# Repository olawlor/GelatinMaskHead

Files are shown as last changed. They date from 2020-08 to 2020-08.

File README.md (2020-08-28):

# Gelatin Mask-testing Head
For quantitative testing of masks, the standard NIOSH head models are made from solid rigid plastic.  Because this does not at all resemble human skin, the NIOSH N95 testing protocol allows the use of rope caulk and tape to provide a tight seal, which is not a good approximation for a human face.

This project contains a 3D printed set of parts and molds for casting a gelatin face for testing masks.  Because the face is cast from soft flexible gelatin, this better matches the compliance of a human face, which should give more accurate results when testing masks for fit and filtering effectiveness.

The face outer surface is currently built around the NIOSH "medium" head profile.

See the NioshMedium/ directory for CAD files of:
 * The "Head" without a face.  The head is normally printed from rigid plastic and holds the face in place, and provides a place for mask straps to attach.  There is a six-bolt hole pattern in the bottom of the head for mounting it into a test apparatus.  The top of the head is open to allow access to the back of the face, such as flowing in aerosols.
 * The "Skull" that gets bolted inside the face area.  This is printed from rigid plastic, and models the actual human skull areas that support the face while wearing a mask.
 * The "Overmold" is used to cast gelatin onto the skull while mounted on the head.
 
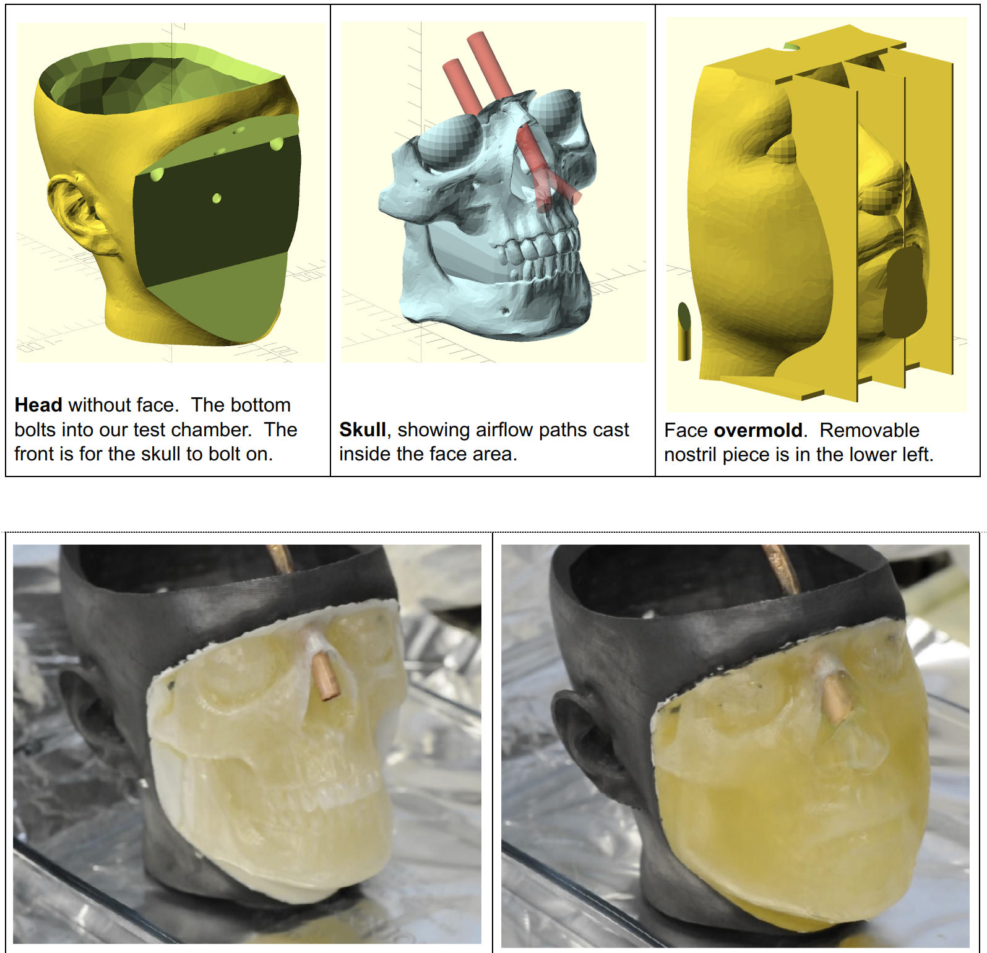
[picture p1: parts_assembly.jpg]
Components to 3D print, and the resulting molded head.


All of these parts should be printed as smooth and watertight as possible--casting gelatin will leak into non-watertight areas, resulting in much larger gelatin consumption.  The no-leak gelatin volume is 310cc, but 500cc is reasonable to account for leaks and spills.  Pre-chilling the mold can help somewhat with leaks.

After printing, the face overmold should be sealed and smoothed by applying several layers of high-build automotive primer paint.  A release layer of vaseline dissolved in volatile lamp oil should be applied to the inside of the face overmold.  The skull is then bolted to the face with a ¼" or 6mm plastic bolt (plastic is preferred over metal to reduce galvanic effects around the salty gelatin).

The air inlet tubes for the nostril or mouth inlets are ⅜" or 10mm outside diameter.  Conductive silicone is recommended: nonconductive plastic can accumulate an electrostatic charge, and metals can corrode.  The air inlet tub is inserted and aligned with the nostril plugs (verify inlet to nostril alignment with a lamp behind the overmold before pouring).  The inlet tube should be filled with a temporary ¼" or 6mm plastic tube to prevent it from getting filled with gel during casting.

The castable gelatin face composition is primarily water, with:
 * 10% w/v gelatin (Knox gelatin.  10% is the US federal standard ballistics testing gelatin concentration but is rather delicate; it may be worthwhile to upgrade this to 20% NATO gelatin for better handling properties.)
 * 10% w/v table salt, for electrical conductivity and biological decay resistance
 * 1% w/v sodium bicarbonate, to remain alkaline which increases the gelatin strength and reduces metal corrosion from the salt.  The solution is still quite corrosive, even to copper.

Casting protocol:
 * Mix gelatin with cold (5C) water first (like flour, the outside of a dry area will gel and prevent water accessing the interior unless you start cold).
 * Heat the gelatin to 45C, stir until gelatin is fully dissolved, add salt, stir until fully dissolved, filter
 * Ensure the overmold is face-down, with the head and skull inserted completely, and the nostril inlet tube aligned with the nostril plugs.
 * Carefully pour gelatin into the mold at about 30C gelatin temperature.
 * Chill the mold 10C for several hours to fully solidify before demolding.  The head needs to be treated gently, and kept in a cool environment: in a warm sunbeam for several hours it will melt off the skull.

Spray a clear rubbery sealant (Rustoleum LeakSeal, clear) directly onto the gelatin surface of the face to create a thin (approx 0.2mm) "skin" layer over the gelatin.  This substantially reduces abrasion damage to the face's surface while putting masks on and taking masks off, and has the added benefit of reducing water evaporation losses from the gelatin surface.  Masks also seem to seal better (by about 10%) against this surface than the bare gelatin.

The salt makes the face electrically conductive, but the plastic of the head is nonconductive, and hence static susceptible.  To reduce static, the hard plastic parts were fully painted in a dark graphite slurry consisting of:
 * Conductive finely ground graphite (agricultural EZ-Slide brand)
 * Acetone solvent
 * ABS 3D printer filament, chopped into pieces and dissolved into the acetone, to bind the dried graphite.
This combines to a sort of thin paint, although the graphite settles out rapidly and must be stirred up regularly.  Apply this fairly heavily and then buff off excess with steel wool, making a dark and rather metallic looking finish that electrically reads in the kilo-ohm range.

Explanation of these files and initial mask testing results are here:
https://docs.google.com/document/d/1Q9jaSaZRyKj-hi1BDpFaLHJNcuCx2OrSKFoyBqVJWUo/edit

"Human_Skull_Scan_fixed2" is a human skull model, license CC-A-NC, modified from:
    https://www.thingiverse.com/thing:2368585

This model was prepared by Orion Lawlor, lawlor@alaska.edu, in summer 2020 to help with COVID prevention.  Support for this project has been provided by the Office of Naval Research.

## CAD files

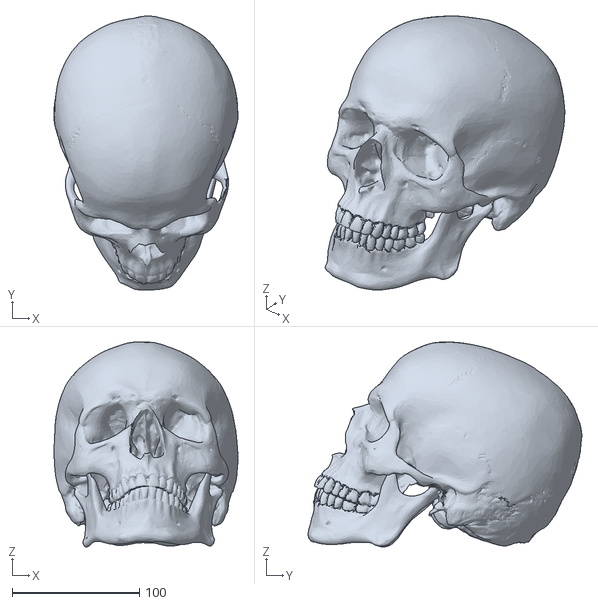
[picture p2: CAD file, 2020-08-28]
Human_Skull_Scan_fixed2.stl
144.8 x 215.6 x 161.4

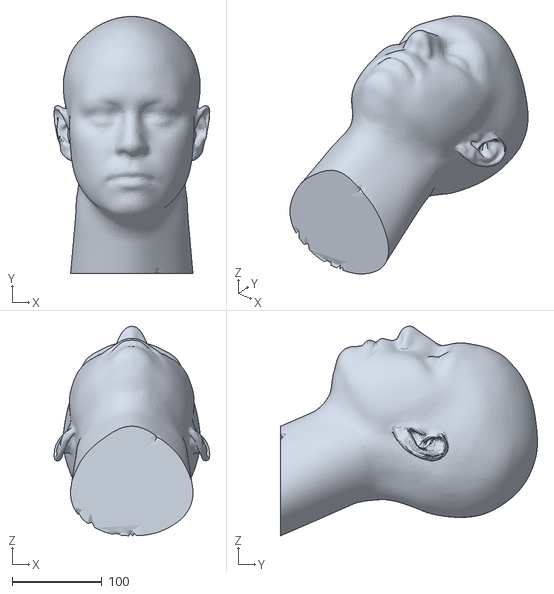
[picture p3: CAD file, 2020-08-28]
NioshMedium/8-NIOSH_medium_20k.stl
173.0 x 285.7 x 233.0

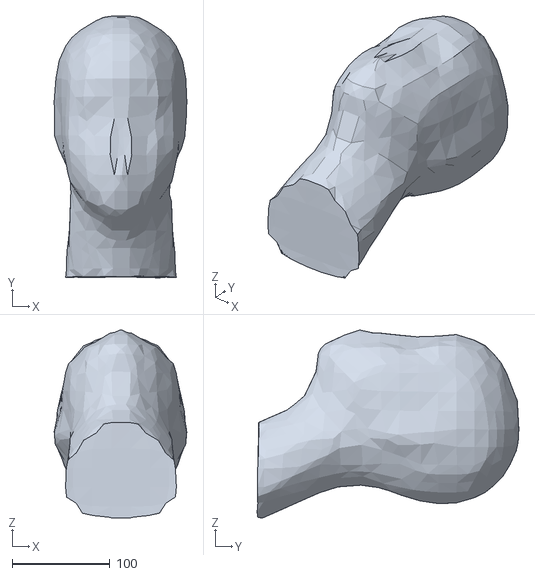
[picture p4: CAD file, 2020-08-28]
NioshMedium/8-NIOSH_medium_interior.stl
135.8 x 268.0 x 192.5

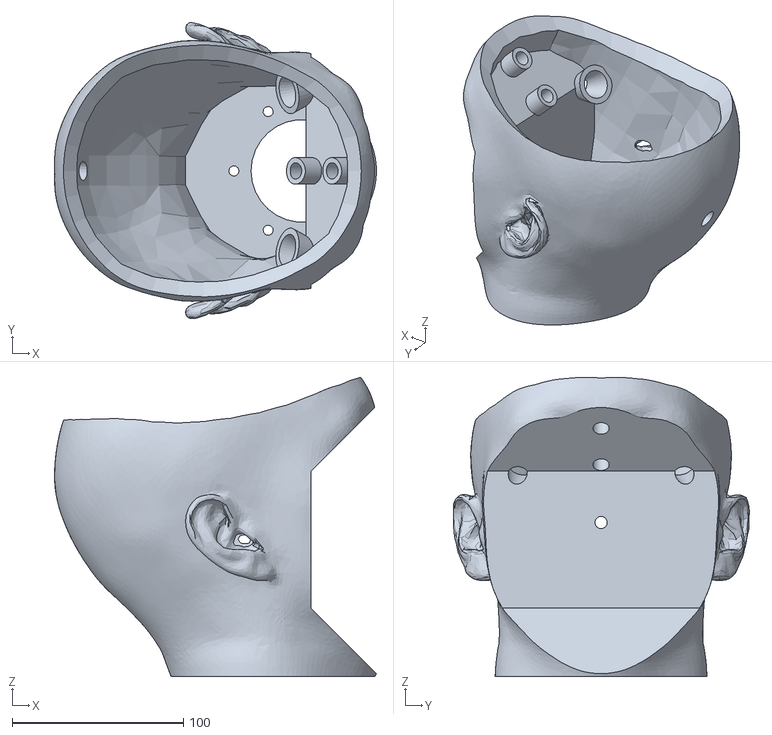
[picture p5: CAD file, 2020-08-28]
NioshMedium/medium_head.stl
188.0 x 173.0 x 174.8

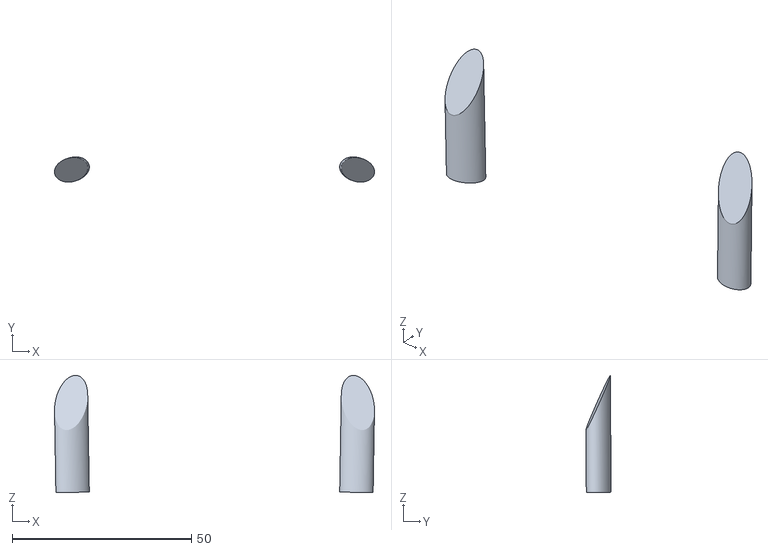
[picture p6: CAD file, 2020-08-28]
NioshMedium/medium_nostril_tubes.stl
89.3 x 7.02 x 32.7

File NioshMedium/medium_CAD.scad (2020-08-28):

/*
Human head with rubbery castable face and anatomical underlying skull.
Designed for COVID prevention mask testing.

Explanation of this file and initial testing results:
https://docs.google.com/document/d/1Q9jaSaZRyKj-hi1BDpFaLHJNcuCx2OrSKFoyBqVJWUo/edit#

Rev 2, with:
	- Face overmold points the opposite direction, so it's hairy on non-cast side.

Dr. Orion Lawlor, lawlor@alaska.edu, updated 2020-06-23

Source files needed:
"Human_Skull_Scan_fixed2" is CC-A-NC modified from:
    https://www.thingiverse.com/thing:2368585

"8-NIOSH-Medium" is from the standard NIOSH mask testing head model,
size "medium", from the "fit2face challenge" data packet:
    https://www.americamakes.us/fit2face/

*/

inch=25.4;


// Skull, scaled to real size and lined up with head
module skull() {
	rotate([0,0,90-3])
	rotate([5,0.5,1])
	translate([-5.5,-10,35])
	scale([1.05,1.05,1.05])
	import("./Human_Skull_Scan_fixed2.stl",convexity=8);
}

// Spacers to take up space of eyes and tongue in skull
module skull_spacers() {
	
	// Tongue area spacer
	hull() {
		// Smaller front sphere
		translate([80,0,65])
			scale([1,0.8,1])
				sphere(d=75);
		// Larger back sphere
		translate([40,0,75])
			scale([1,1,1])
				sphere(d=95);
	}
	
	// Eyeballs, extra-large for mold indexing
	ipd=62; // inter-pupillary distance
	for (side=[-1,+1])
	translate([66,ipd/2*side,130])
		sphere(d=36);
}


// Fix orientation of head to standard printable
module niosh_to_standard() {
	translate([10,0,90])
	rotate([0,-25,0])
	rotate([0,90,0])
	rotate([0,0,90])
	 children();
}

module niosh_inside() {
	niosh_to_standard()
		import("./8-NIOSH_medium_interior.stl",convexity=2);
}
module niosh_outside() {
	niosh_to_standard()
		import("./8-NIOSH_medium_20k.stl",convexity=6);
}

// Skull, trimmed by niosh outer surface
module skull_trimmed() {
	intersection() {
		skull();
		translate([-1,0,0])
			niosh_outside();
	}
}

module niosh(cutaway=0) {
	difference() {
		niosh_outside();
		niosh_inside();
		
		if (cutaway) cube([1000,1000,1000]);
	}
}

// Lawlor head, for comparison (bolts, clearance, etc)
//module lawlor_head() {
//	import("../head_vase.stl");
//}

// Illustrates head with skull inside
module illustration(cutaway=0) {
	union() {
		skull_trimmed();
		#niosh(cutaway);
		// #lawlor_head();
	}
}


// X coordinate of start of face (back side)
face_casting_start_x=50;
face_casting_center_z=80;

nose_air_tube_z=150;

face_mounting_bolt_z=50;

// Forward area of face for casting
module face_casting_zone(inset=0) {
	hull() 
	for (diagonal_chin=[0,40])
	for (diagonal_eyes=[0,40])
	{
	translate(
		[face_casting_start_x+diagonal_chin+diagonal_eyes+1000,
		 0,
		 face_casting_center_z-diagonal_chin+diagonal_eyes]
		) 
		cube([2000-2*inset,2000-2*inset,80-2*inset],center=true);
	}
}



// Cast-in copper tubing (nose air inlet)
breathing_start=[75,0,145];
breathing_rotate=[0,-45,0];
airtube_OD=3/8*inch;
airtube_long=80;
module nose_air_tube(fatten=0,upshift=0) {
	
	for (nose0mouth1=[0,1]) {
	translate(breathing_start)
	//translate([face_casting_start_x,0,nose_air_tube_z])
	rotate(breathing_rotate)
		translate([nose0mouth1*-30,0,upshift])
		cylinder(d=airtube_OD+2*fatten,h=airtube_long-2*fatten,center=true,$fs=0.1,$fa=2);
	}
}

// Each individual nostril uses one of these tubes
nostril_flareout=[25,10,0]; // rotation per nostril
nostril_len=25;
module nostril_tube(clearance=0.0) {
	difference() {
		rotate([180,0,0])
		rotate(nostril_flareout)
			rotate([0,0,20])
			scale([1,0.7,1])
				cylinder($fs=0.1,$fa=2,d=airtube_OD+2*clearance,h=2*nostril_len,center=true);
		
		// Put in bilateral symmetry plane
		translate([0,-1000,0]) cube([2000,2000,2000],center=true);
		// Put in flared copper tubing
	}
}
// put nostril tube flat along Z axis again
module nostril_tube_undo() {
	translate([0,0,nostril_len])
	rotate([180,0,0])
	rotate(-nostril_flareout)
	rotate([180,0,0])
		children();
}

// Nostril holes are loose pieces cast into the face
module nostril_holes(clearance=0.0) {
	#for (side=[-1,+1]) scale([1,side,1])
	{
		translate(breathing_start)
		rotate(breathing_rotate)
		translate([0,0,-airtube_long/2])
			nostril_tube(clearance);
	}
}

// Mounting hole to bolt skull to head.
//  Tapped into plastic of skull
//  Goes clear through back of head, to allow tool to be inserted
module skull_mount_hole(clearance=0.2) {
	translate([face_casting_start_x+20,0,90])
		rotate([0,-90,0])
			cylinder(d1=0.25*inch+clearance,d2=12,h=180);
}

// Head non-printable areas
module head_holes(inset=0) {

	// Below head is nonprintable
	translate([0,0,inset-1000]) cube([2000,2000,2000],center=true);
	
	// Face area is printed separately (minus sign so back wall is solid)
	face_casting_zone(-inset);
	
	// Top access, also prevents overhang issues inside
	base=100; // start diameter of flared opening
	height=300; // height of flared area
	translate([-20,0,125+0.01*inset])
		cylinder(d1=base-2*inset,d2=base+2*height-2*inset,h=height);
}

// Main opening and mounting holes in bottom
module mounting_holes() {
	translate([45,0,-1]) linear_extrude(height=10) {
		circle(d=60);
		nbolts=6;
		for (angle=[120:360/nbolts:300-1])
			rotate([0,0,angle]) translate([40,0,0])
				circle(d=6);
	}
}

// Holes for pouring in castable face material
module face_fill_holes(inset=0) {
	for (side=[-1,+1]) scale([1,side,1])
		translate([55,50,115])
			rotate([0,-60,0])
			rotate([10,0,0])
				cylinder(d1=8+2*inset,
					d2=20+2*inset,
					h=25-inset);
}



// Head with hole for face
wall=3;
module head_without_face() {
	difference() {
		// Start with the exterior
		difference() {
			niosh_outside();
			head_holes();
		}
		
		// Clear out the interior
		difference() {
			niosh_inside();
			head_holes(wall);
			nose_air_tube(wall);
			face_fill_holes(wall);
		}
		
		// Final holes
		nose_air_tube();
		face_fill_holes();
		mounting_holes();
		skull_mount_hole();
		
		// Cutaway (illustration)
		// cube([200,100,200]);
	}
}

// Castable face (for volume estimate)
module face_castable() {
	difference() {
		intersection() {
			niosh_outside();
			face_casting_zone();
		}
		
		skull_trimmed();
		skull_spacers();
		nostril_holes();
	}
}

// Bones in face
module face_bones() {
	difference() {
		intersection() {
			union() {
				skull_trimmed();
				skull_spacers();
			}
			face_casting_zone(0.1);
		}
		
		nose_air_tube();
		skull_mount_hole(-1.5);
	}
}
// Back lying flat on build plate
module face_bones_printable() {
	translate([-80,0,0])
	rotate([0,-90,0])
	translate([-face_casting_start_x-0.1,0,0])
		face_bones();
}

// Outside casting block for face:
//   holds the castable face material in place.
casting_block_xlo=35;
casting_block_zlo=-wall;
casting_block_zhi=180;

module make_shear(p) {
   multmatrix([
		[1,0,p,0],
		[0,1,p,0],
		[0,0,1,0]
	  ]) children();
}

module casting_block_size() {
	translate([casting_block_xlo,-100,casting_block_zlo])
		//make_shear(-0.1)
			cube([100,200,casting_block_zhi-casting_block_zlo]);
}

// Outside of NIOSH head, enlarged slightly
module niosh_outside_enlarged() {
	for (xdel=[0,40])
	for (zdel=[0,50]) {
		scale_center=[20+xdel,0,80+zdel];
		s=1+2*wall/70;
		translate(+scale_center)
		scale([s,s,s])
		translate(-scale_center)
		{
			niosh_outside();
			skull_spacers();
		}
	}
}

// Lies flat and hold the liquid as the face is cast.
//  Removed from the final print.
module overmold() {
	// Flat base (and neck closure)
	bottom_x=75;
	translate([casting_block_xlo+bottom_x/2,0,casting_block_zlo+wall/2])
		cube([bottom_x,120,wall],center=true);
	
	// Flat top (and top closure)
	top_x=50;
	difference() {
		translate([casting_block_xlo+top_x/2,0,casting_block_zhi-wall/2])
			cube([top_x,110,wall],center=true);
		
		// Let air tube clear top plate
		nose_air_tube(wall,20);
	}
	
	difference() {
		intersection() {
			union() {
				// outer face surface
				niosh_outside_enlarged();
				
				// Extra meat around nostrils, so no leaks
				translate([115,0,110])
					sphere(d=37);
				
				// support to let us sit face-down
				for (sup=[-1,0,+1])
					translate([0,sup*40,0])
						cube([1000,wall/2,1000],center=true);
				
			}
			casting_block_size();
		}
		
		// Clearance inside for actual face
		niosh_outside();
		skull_spacers();
		nostril_holes(0.2);
		
		// Cutaway (illustration / debugging)
		//translate([100,10,0]) cube([1000,1000,1000]);
	}
	
}

module nostril_tubes_printable() {
		for(side=[-1,1]) scale([side,1,1])
			translate([40,0,0])
				nostril_tube_undo() nostril_tube();
	
}
module overmold_printable() {
	translate([-100,225,wall]) rotate([0,0,270])
	{
		overmold();
		translate([0,0,-wall]) rotate([0,0,90]) nostril_tubes_printable();
	}
}


bone_color=[0.7,0.9,0.9];
module one_plate_printable() {
	head_without_face();
	
	casting_block_printable();
	color(bone_color) face_bones_printable();
}

module demo_head() {
	//#face_castable();
	//head_without_face();
	
	color(bone_color) face_bones();
	
	#nostril_holes();
	#nose_air_tube();
	//#casting_block();
}

// demo_head();
// one_plate_printable();
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
